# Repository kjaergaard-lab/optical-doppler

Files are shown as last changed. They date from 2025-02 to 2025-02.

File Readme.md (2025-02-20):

# Translation Stage for the optical Doppler effect

Originally this experiment used a stepper motor, which has substantial vibration at lower speeds. The documentation for this version is in the `OLDStepperMotorVariant`. 

The details of the servo motor setup is in the `StepperServoConversion` folder.

The current code is in `pio-grbl`. This device runs a modified version of the GRBL CNC control software, and the folder here is setup to use PlatformIO to manage compiling and uploading.

In config.h, the line
`#define CUSTOM_VARIABLE_SPEED_CYCLE`
enables code which:

- Performs a homing cycle at reset (i.e. runs the stage into the limit switch so it knows where the end of the rail is)
- The moves back and forth along the rail
- While reading the voltage on the potentiometer in order to scale the motion speed.

If this line is commented out, then the result is standard [GRBL](https://github.com/gnea/grbl/wiki) behaviour (with only an x axis). This means that nothing will happen on reset, and it will wait for G code commands on the USB serial interface (115200 baud).

As well as the settings in config.h, [GRBL has settings which may be updated without programming the device.](https://github.com/gnea/grbl/wiki/Grbl-v1.1-Configuration) See [Config.md](Config.md) for more details.

## Schematic

Electronic schematic of the controller is in [StepperServoConversion/ServoGrblBoard](StepperServoConversion/ServoGrblBoard)

## Troubleshooting

#### Device does nothing at startup

- Confirm that Emergency Stop button is not depressed
- Check that the power switch at the rear of the unit is turned on
- Check that power is actually being supplied
- Make sure that the limit switch on the rail isn't already being pressed.

If all of these are fine, open the lid of the device (WARNING: MAINS VOLTAGES INSIDE), and confirm that the red LED display on the servo controller (located near the emergency stop switch) is lit, and that the arduino unit also has a green power LED lit.

- Connect a USB C cable to the arduino (CH340 USB-serial converter), and connect to the serial port with 115200 baud. The arduino should reset on connect, and one can note any errors that may be reported.
- Check that the GRBL configuration is correct (request config by sending `$$`), especially the speed ($110). See [Config.md](Config.md) for more details.

#### The device perform a homing cycle (runs the stage into the limit switch) and then does nothing

 - This implies that everything is powered, and that the arduino running GRBL is communicating effectively with the servo controller
 - If you can still hear the whine of the servo controller after homing, then GRBL still thinks it is moving the stage
    - Ensure that the speed potentiometer isn't set to 0
    - Take the top of the unit off (WARNING: MAINS VOLTAGES INSIDE), and confirm that the voltage at A0 on the arduino is non-zero
    -  Connect a USB C cable to the arduino (CH340 USB-serial converter), and connect to the serial port with 115200 baud. Check that the GRBL configuration is correct (request config by sending `$$`), especially the speed ($110). See [Config.md](Config.md) for more details.
 - If you can't hear the whine of the motor, GRBL has decided to stop controlling the motor, presumably due to an error condition
    - Connect a USB C cable to the arduino (CH340 USB-serial converter), and connect to the serial port with 115200 baud. The arduino should reset on connect, and one can note any errors that may be reported.

#### The speed of the stage isn't consistent / smooth

 - Check the potentiometer connections and health. Consider replacing, and/or adding mor filtering.

#### The stage runs into the end
   *YOU SHOULD IMMEDIATELY HIT THE EMERGENCY STOP BUTTON IF THE DEVICE DOESN'T IMMEDIATELY STOP ITSELF* 

 - Manually move the stage off the limit switches (most easily by twisting the lead screw near the motor where there isn't any grease), and reset the controller while watching in case it happens again.
 - If it happens during the intial homing stage (and runs into the switch), check the limit switch connection, which has possibly somehow failed short.
 - Consider reprogramming and reconfiguring the internal arduino as above.

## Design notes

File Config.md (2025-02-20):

# GRBL configuration

The configuration loaded into grbl can be listed by sending the `$$` command. Note that the stage will try to home before it will respond to serial commands, so if you have the lid off the stage controller, you probably don't want to be powering the device with mains. The arduino can be powered by the USB C cable. Connect to the arduino serial (115200 baud rate), and the GRBL welcome should pop up. After waiting a second, tap the limit switches on the stage twice to trick it into thinking that it has homed successfully, and it should respond to commands. 

The configuration loaded initially is as follows.

```
$0=10
$1=25
$2=0
$3=0
$4=0
$5=1
$6=0
$10=1
$11=0.010
$12=0.002
$13=0
$20=0
$21=1
$22=1
$23=1
$24=25.000
$25=500.000
$26=250
$27=1.000
$30=1000
$31=0
$32=0
$100=1000.000
$101=250.000
$102=250.000
$110=2000.000
$111=500.000
$112=500.000
$120=200.000
$121=10.000
$122=10.000
$130=235.000
$131=1.000
$132=1.000
```

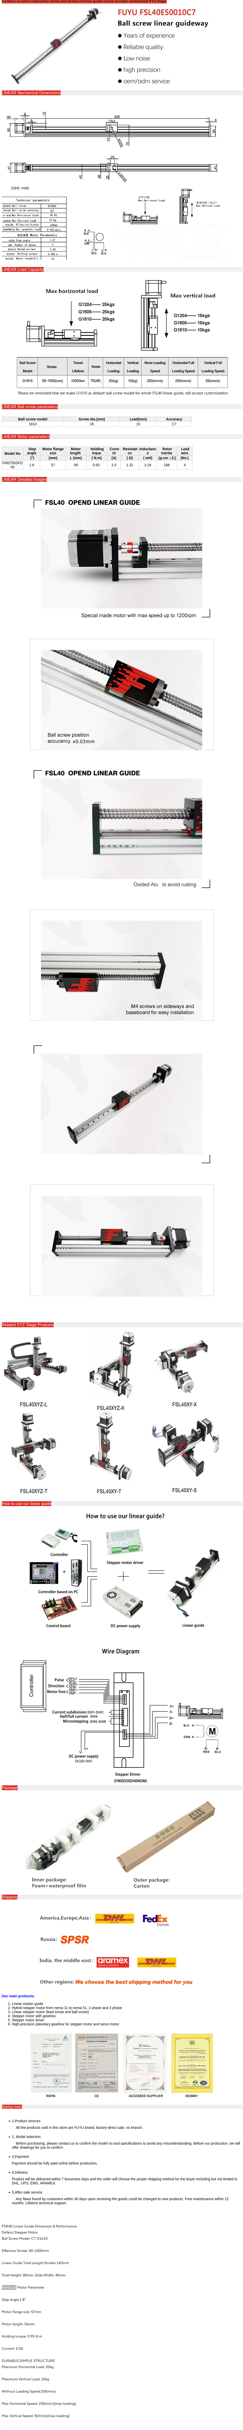
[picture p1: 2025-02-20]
StepperServoConversion/StepperDetails.png

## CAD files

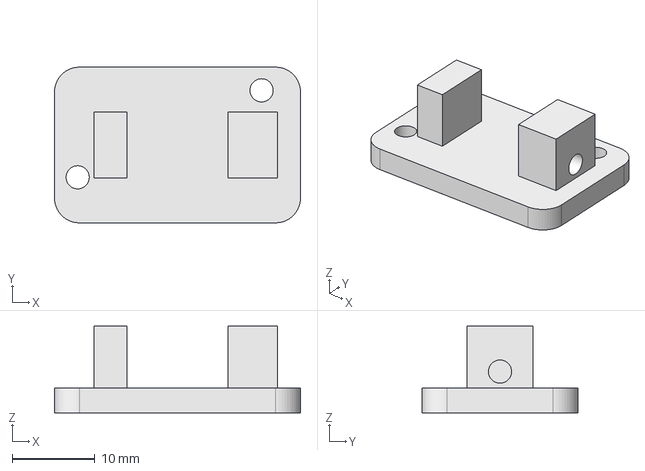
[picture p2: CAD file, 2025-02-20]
OLDStepperMotorVariant/SwitchMount.FCStd
29.7 x 18.8 x 10.5 mm

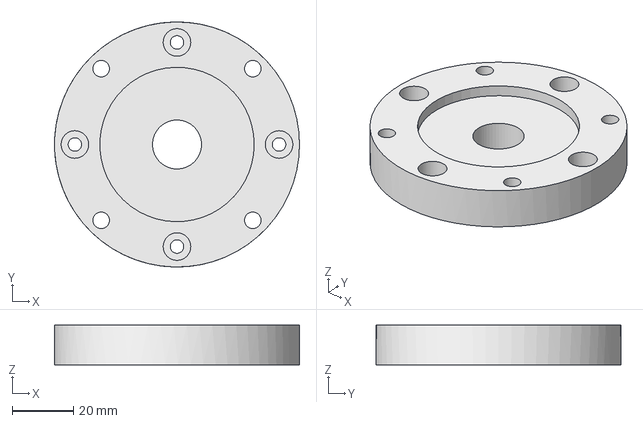
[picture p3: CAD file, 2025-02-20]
StepperServoConversion/AdapterPlate.FCStd
80.0 x 80.0 x 13.0 mm

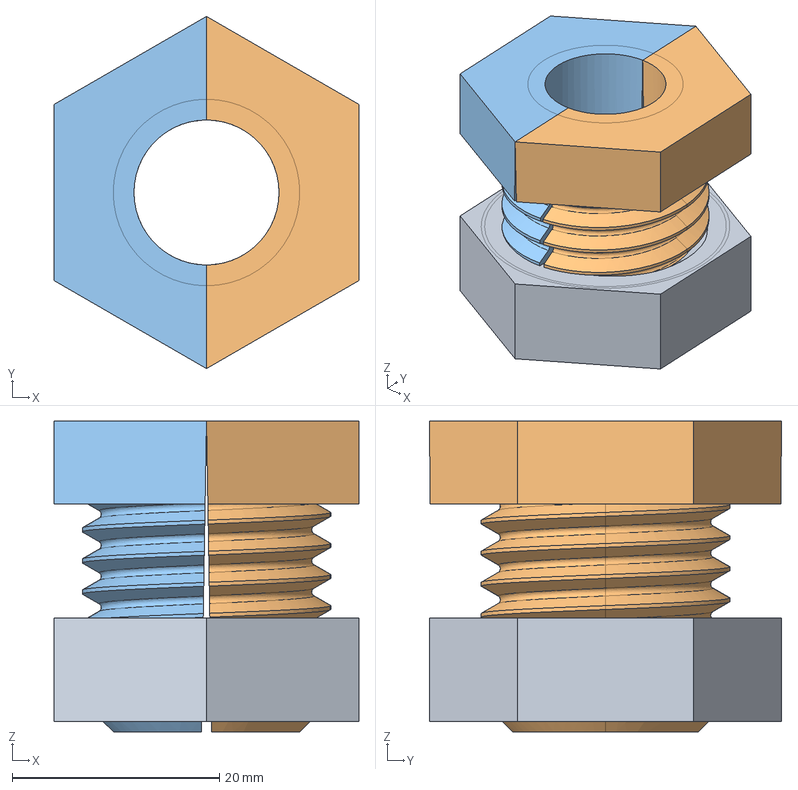
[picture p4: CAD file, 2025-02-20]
StepperServoConversion/SplitGrommet.FCStd
29.4 x 34.0 x 30.0 mm
Nut
Side003
Side004

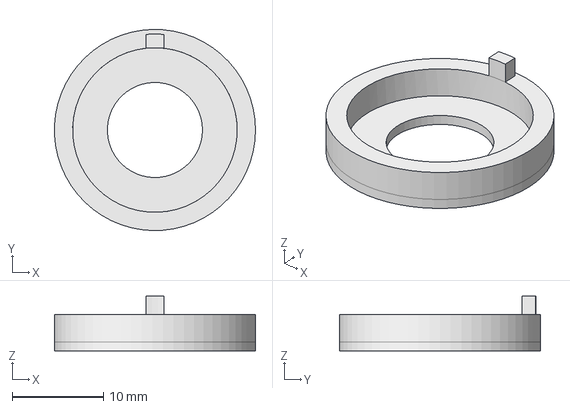
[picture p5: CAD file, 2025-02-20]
StepperServoConversion/PotDialLocator.FCStd
22.0 x 22.0 x 6.00 mm

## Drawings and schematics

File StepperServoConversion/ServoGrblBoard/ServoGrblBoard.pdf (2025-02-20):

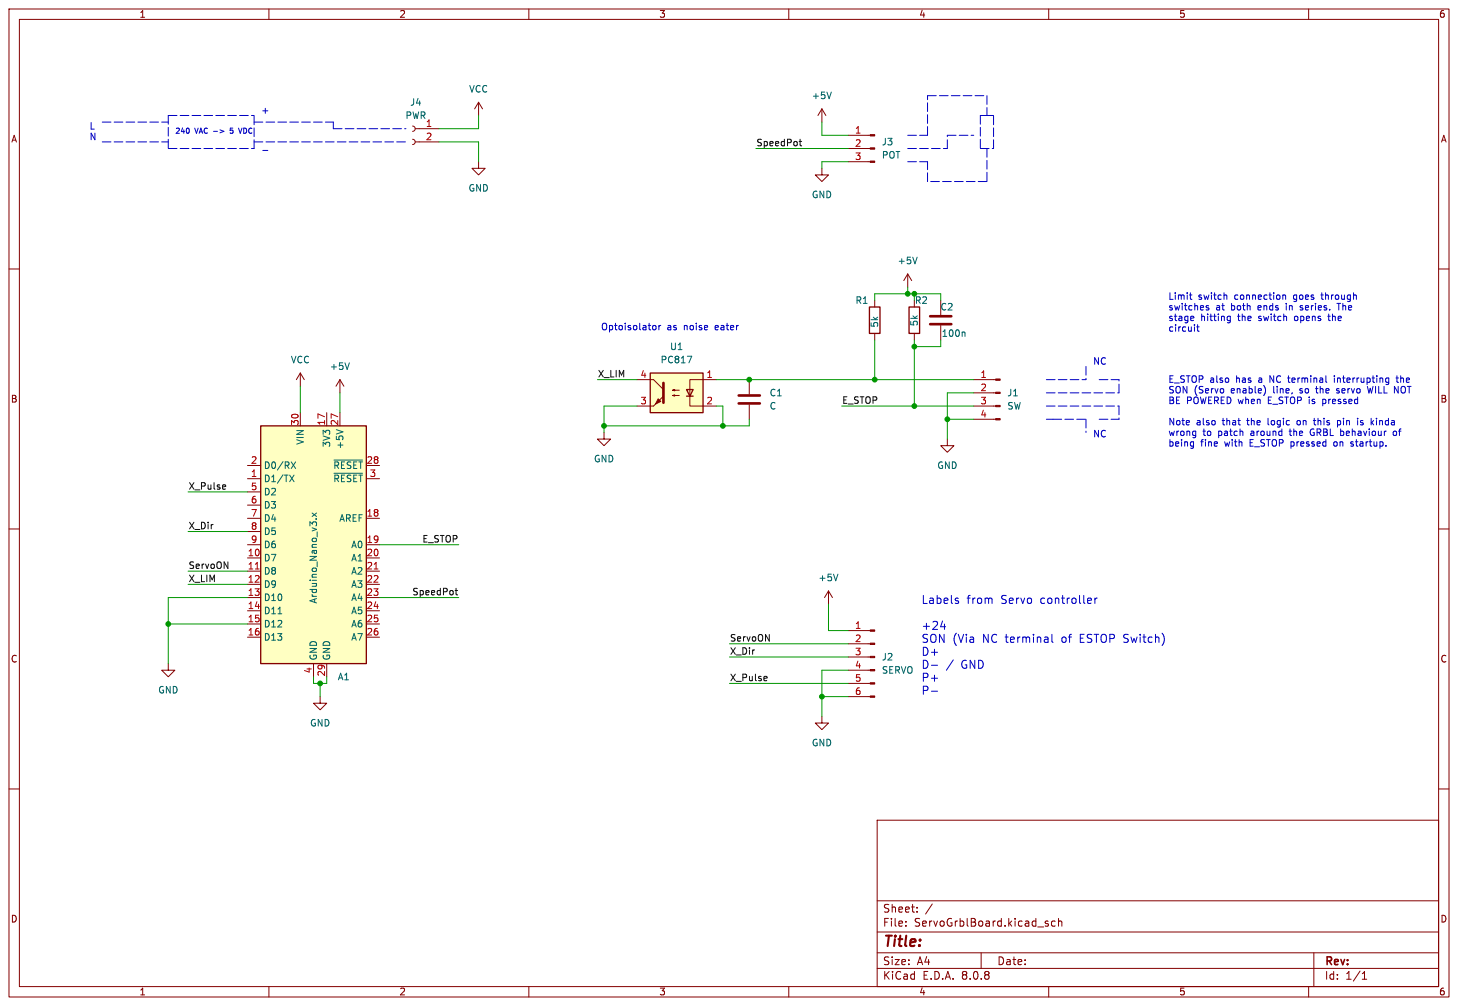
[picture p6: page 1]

switches at both ends in series. The
circuit
